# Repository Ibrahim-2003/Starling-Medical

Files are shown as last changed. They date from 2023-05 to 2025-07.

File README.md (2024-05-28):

# Starling Medical Local Repo
This is a repo of the work I did at Starling Medical during my internship. Included in this repo:
- Datasheets of the electronics I used in my projects
- Engineering drawings for manufacturing
- Models of parts and designs I made
- Documentation I wrote for the company
- Notes I took while prototyping and brainstorming
- Research papers I referenced while innovating
- Presentations showcasing my progress and accomplishments
- Programs and software I wrote for the projects

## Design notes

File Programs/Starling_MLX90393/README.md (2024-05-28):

# Adafruit MLX90393 Magnetic Field Sensor Driver Documentation

This driver is for use with the Adafruit MLX90393 Breakout, and has been
designed specifically for these boards:

  ----> https://www.adafruit.com/product/4022

Adafruit invests time and resources providing this open source code,
please support Adafruit and open-source hardware by purchasing
products from Adafruit!

## About this Driver

Originally written by Kevin Townsend for Adafruit Industries. Modified by Ibrahim Al-Akash to meet Starling Medical BPH apparatus requirements.
MIT license, all text above must be included in any redistribution

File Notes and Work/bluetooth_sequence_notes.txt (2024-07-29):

MainActivity.kt
---------------------------------

// onCreate Functions
    BluetoothManagerStateMachine.initialize(applicationContext())
    BluetoothManager2.initialize(applicationContext())
    requestPermissions()

AppSimulationScreen.kt
---------------------------------
Button(
        modifier = Modifier.fillMaxWidth().padding(start = buttonPadding, end = buttonPadding),
        onClick = {
//                navController.previousBackStackEntry?.savedStateHandle?.set("msg", "test data")
//                navController.popBackStack()
        BluetoothManagerStateMachine.startScanning()
        logOutput = "Starting Scan\n" + logOutput
    }) {
        Text(text = "Start")
    }

Gradle
---------------------------------
implementation libs.blessed.kotlin
implementation libs.gson

BluetoothExplorer.kt
---------------------------------
// Press button to turn on scanning in BluetoothManager2
// If the peripheral list in BluetoothManager2 is not empty, display the list of devices using the DeviceNameList which is input to the DeviceNameListHelper
    // Each device gets a DeviceCard using the device name from the DeviceNameListHelper
    // Clicking the DeviceCard stops the scanning in BluetoothManager2, connects to the device using the connectToPeripheral from BluetoothManager2, and navigates to DeviceDetailScreen:
       // BluetoothManager2.stopScanning()
       // val peripheral = BluetoothManager2.peripheralList[index]
       // BluetoothManager2.connectToPeripheral(peripheral)
    // DeviceDetailScreen:
        // Device -> BluetoothManager2.urinDxDeviceCharacteristic
        // Configuration -> BluetoothManager2.urinDxConfigurationCharacteristic
        // Patient -> BluetoothManager2.urinDxPatientCharacteristic
        // Sensors Record {CharacteristicReadInteractionCard} -> BluetoothManager2.urinDxSensorsRecordCharacteristic
        // Network Record {CharacteristicReadInteractionCard} -> BluetoothManager2.urinDxNetworkRecordCharacteristic
        // Battery Record {CharacteristicReadInteractionCard} -> BluetoothManager2.urinDxBatteryRecordCharacteristic
        // Debug {CharacteristicReadInteractionCard} -> BluetoothManager2.urinDxDebugCharacteristic

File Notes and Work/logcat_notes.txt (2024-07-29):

STARTUP SEQUENCE
-----------------------------------------------------------------------------
BluetoothManagerStateMachine,initializing BluetoothHandler
BluetoothManager2,initializing BluetoothHandler
ProfileInstaller,Installing profile for com.starling.bluetoothexplorer
BluetoothAdapter,isLeEnabled(): ON

PRESS START
-----------------------------------------------------------------------------
BluetoothLeScanner,onScannerRegistered() - status=0 scannerId=6 mScannerId=0
BluetoothManagerStateMachine,Found peripheral 'UrinDx' with RSSI -57
BluetoothManagerStateMachine,Connecting to peripheral UrinDx
BluetoothAdapter,isLeEnabled(): ON
BluetoothGatt,connect() - device: CC:11:E1:27:24:1D, auto: false
BluetoothGatt,registerApp()
BluetoothGatt,registerApp() - UUID=1f0445b1-f4ec-49c2-9a09-b407b8ef458b
BluetoothGatt,onClientRegistered() - status=0 clientIf=6
BluetoothGatt,onClientConnectionState() - status=0 clientIf=6 device=CC:11:E1:27:24:1D
BluetoothGatt,discoverServices() - device: CC:11:E1:27:24:1D
BluetoothGatt,onConnectionUpdated() - Device=CC:11:E1:27:24:1D interval=6 latency=0 timeout=500 status=0
BluetoothGatt,onPhyUpdate() - status=0 address=CC:11:E1:27:24:1D txPhy=2 rxPhy=2
BluetoothGatt,onSearchComplete() = Device=CC:11:E1:27:24:1D Status=0
BluetoothManagerStateMachine,Connected to 'UrinDx'
BluetoothManagerStateMachine,Discovered service 00001801-0000-1000-8000-00805f9b34fb
BluetoothManagerStateMachine,Discovered service 00001800-0000-1000-8000-00805f9b34fb
BluetoothManagerStateMachine,Discovered service 0000180f-0000-1000-8000-00805f9b34fb
BluetoothManagerStateMachine,Discovered service 14700001-0eed-456e-a568-7e4e17683148
BluetoothManager,Found characteristic 14700002-0eed-456e-a568-7e4e17683148
BluetoothManagerStateMachine,Discovered service 8d53dc1d-1db7-4cd3-868b-8a527460aa84
BluetoothGatt,requestConnectionPriority() - params: 1
BluetoothGatt,onConnectionUpdated() - Device=CC:11:E1:27:24:1D interval=39 latency=0 timeout=500 status=0
BluetoothGatt,setCharacteristicNotification() - uuid: 14700005-0eed-456e-a568-7e4e17683148 enable: true
BluetoothManagerStateMachine,SUCCESS: Notify set to true for 14700005-0eed-456e-a568-7e4e17683148
BluetoothManagerStateMachine,SUCCESS: Notify set to true for Patient Sample Characteristic
BluetoothGatt,onConnectionUpdated() - Device=CC:11:E1:27:24:1D interval=12 latency=0 timeout=500 status=0
BluetoothGatt,onConnectionUpdated() - Device=CC:11:E1:27:24:1D interval=12 latency=0 timeout=400 status=0
BluetoothManagerStateMachine,Received urinDxPatientSampleCharacteristic
BluetoothManagerStateMachine,[B@92c0d03
BluetoothManagerStateMachine,000051a23aff900100000000000000000000000000000000000000000000000000000000000000000000000000000000000000008c093e074b081404ef064f0b5a093e0748081004ef06390b55093e0747080c04f3061e0b53093e0747080b04f206340b52093e0746080a04f6063a0b51093e0746080a04fb06370b0000000000000000000000000000000000000000000000000000000000000000000000000000000000000000000000000000000000000000000000000000000000000000000000000000000000
BluetoothGatt,onClientConnectionState() - status=19 clientIf=6 device=CC:11:E1:27:24:1D
BluetoothGatt,close()
BluetoothGatt,unregisterApp() - mClientIf=6
BluetoothManagerStateMachine,disconnected 'UrinDx'

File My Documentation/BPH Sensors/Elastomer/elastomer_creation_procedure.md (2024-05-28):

# How to Make an Elastomer for Magnetic BPH Sensor
## Starling Medical
### Ibrahim Al-Akash

# Elastomer Creation Procedure

## Overview
First, model the elastomer with the appropriate geometry for your test. Next, 3D print the elastomer mold. Then, cast the mold using the silicone of the appropriate durometer for your test. Finally, assemble the elastomer with the appropriate magnet for your test.

## Modeling and 3D Printing
1. Design elastomer geometry in SolidWorks. Refer to the file `elastomer_notes.md` or `elastomer_notes.pdf` for further details on how to design an elastomer geometry.
2. Save SolidWorks design as an `.STL` file and import to Chitubox software.
3. In Chitubox software, apply a tilt if possible to the model (for example rotate around z-axis by 45 degrees) and the add supports to model.
4. Ensure the correct resin profile is selected so that the profile matches the resin you will be printing with. Ensure the correct printer is selected in the Chitubox settings.
5. Slice the model and inspect it for any artifacts or errors. If there are errors, try rotating along a different axis and reapplying the supports.
6. Export the slice which will be a `.CTB` file to the directory of your choosing.
7. Upload the exported slice file to a USB flashdrive to send to the 3D printer.
8. Ensure the 3D printer has enough resin to print the parts.
9. Begin the print on the 3D printer.
10. When the 3D print is completed, carefully remove the parts from the plate by using the metal spatula. If the part is stuck, spray a little isopropyl alcohol on it and try again.
11. There should be 3 containers next to the 3D printers labeled `99% Isopropyl Alcohol`, `99% Isopropyl Alcohol (Contaminated)`, and `Diluted Green Wash`. Thoroughly clean the printed parts in each bucket in this order.
12. Set the parts next to the fan and wait ~5 minutes to dry.
13. Place the parts in the water cage in the container at the curing station. Remove the curing plate from the machine and place the water container in its place. Close the lid on it. Make sure the curing machine is set to rotation mode, not light mode. Set the time to 5:00 (6:00 if there are a lot of parts) and let the machine rinse the parts.
14. Once the rinse step is completed, set the parts next to the fan and wait 10 to 15 minutes until they are dry.
15. Once the parts are finished, place the curing plate on the curing machine. Ensure the magnets are aligned correctly so the plate is flush against the base. Ensure the curing machine is set to light mode. Set the time to 5:00 if you are using a VytaFlex or other tin-based silicone. If you are using an ExoFlex or other platinum-based silicone, set the time to as long as possible.
16. Once the curing is completed, carefully remove the supports from the parts using pliers.

## Casting the Silicone Mold
### EcoFlex or Platinum-Based Silicone
1. Spray acryllic lacquer onto the 3D printed molds and ensure any surface that will come into contact with the silicone is sufficiently covered with the lacquer. Wait 24 hours for the acryllic lacquer to cure properly. *This step is critical because platinum-based silicone does not cure well when in contact with the resin. You must disrupt the chemical interaction in order for the silicone to cure properly*.
2. Apply a light coat of MAN200 Releasing Agent to the 3D printed molds.
3. Thoroughly stir Part A and Part B silicones with a popsicle stick prior to dispensing them from their containers. Use separate popsicle sticks for Part A vs. Part B.
4. Ensure you have a scale nearby to measure the Part A and Part B solutions. Place a measuring cup on the scale and tare it. Dispense the appropriate mass of Part A solution into the measuring cup. 
5. Tare the measuring cup with the Part A solution in it. Follow the instructions on the containers to determine the ratio of Part A : Part B by mass. Dispense the appropriate amount of Part B solution into the measuring cup.
6. Thoroghly mix the Part A and Part B mixture using a popsicle stick for 2-3 minutes. The containers for the silicones have a "pot life" specified. This means you can handle the silicones for the specified amount of time before it begins curing.
7. *OPTIONAL*: Place the measuring cup in the vaccum chamber, ensuring the vaccum nozzle is not directly over the cup. Activate the vacuum and wait 3-5 minutes for the bubbles to escape the mixture. *This step is optional, however it produces the best results by removing any bubbles or trapped air from the mixture*.
8. Carefully pour the mixture into the bottom mold until the silicone mixture is flush with the top of the bottom mold. Use a popsicle stick to straighten it out and keep it perfectly flush with the top surface. Then, carefully place the top mold in the approprate position.
9. Wait until the recommended cure time has passed.
10. Carefully open the molds and remove the silicone cast.

### VytaFlex or Tin-Based Silicone
1. Apply a light coat of MAN200 Releasing Agent to the 3D printed molds.
2. Thoroughly stir Part A and Part B silicones with a popsicle stick prior to dispensing them from their containers. Use separate popsicle sticks for Part A vs. Part B.
3. Ensure you have a scale nearby to measure the Part A and Part B solutions. Place a measuring cup on the scale and tare it. Dispense the appropriate mass of Part A solution into the measuring cup. 
4. Tare the measuring cup with the Part A solution in it. Follow the instructions on the containers to determine the ratio of Part A : Part B by mass. Dispense the appropriate amount of Part B solution into the measuring cup.
5. Thoroghly mix the Part A and Part B mixture using a popsicle stick for 2-3 minutes. The containers for the silicones have a "pot life" specified. This means you can handle the silicones for the specified amount of time before it begins curing.
6. *OPTIONAL*: Place the measuring cup in the vaccum chamber, ensuring the vaccum nozzle is not directly over the cup. Activate the vacuum and wait 3-5 minutes for the bubbles to escape the mixture. *This step is optional, however it produces the best results by removing any bubbles or trapped air from the mixture*.
7. Carefully pour the mixture into the bottom mold until the silicone mixture is flush with the top of the bottom mold. Use a popsicle stick to straighten it out and keep it perfectly flush with the top surface. Then, carefully place the top mold in the approprate position.
8. Wait until the recommended cure time has passed.
9. Carefully open the molds and remove the silicone cast.

## Elastomer Assembly
1. Acquire the appropriate magnet for the elastomer and ideally get a magnetic compass to help with properly orienting the magnet prior to adhering it to the elastomer.
2. Ensure the magnet is oriented so that the side of the magnet that attracts the needle North on the compass is facing the sensor as shown in the diagram below:

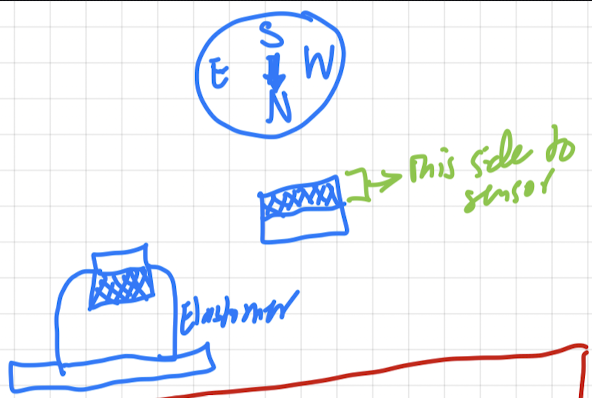
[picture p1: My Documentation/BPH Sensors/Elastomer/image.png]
Magnet Orientation


Alternatively, if you do not have a compass, have the magnetometer sensor running and make sure the magnet is oriented in a way that produces positive B-field values in the magnetometer z-axis data. *This is a very important step. Remember, measure twice and cut once. You must ensure you are certain that the magnet orientation is correct before moving onto the next step*.
3. Apply just enough super glue to adequately cover the surface of the magnet in contact with the elastomer.
4. Wait 10-30 minutes for the super glue to cure.

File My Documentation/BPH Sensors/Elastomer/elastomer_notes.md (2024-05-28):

# How to Design an Elastomer for Magnetic BPH Sensor
## Starling Medical
### Ibrahim Al-Akash

# Elastomer Design Notes

## Overview
To design a proper elastomer for the magnetometer BPH sensor, you must first determine the geometry you want to test, model the elastomer, and model the elastomer mold.

## Elastomer Geometry
Elastomer geometry is important in determining the magnetometer sensitivity. Some basic principles to keep in mind are the following:

- Shorter elastomers are more malleable, however, the magnet has a smaller range of distances it can move. This limits the range of masses the sensor can detect.

- Thicker elastomers enable the magnet to move a larger range of distances, however, they are more rigid. This limits the sensitivity of the magnet, which translates to a lower resolution of masses it can detect (ex: $\pm$ 0.01g vs. $\pm$ 5g).

- Elastomers with a larger surface area in contact with the water will require more water to deform. An equation that is important to keep in mind is $Pressure=\frac{Force}{Area}$. Force is the mass of the water and area is the area of the elastomer in contact with the water. If the area is too large, a very large force will be required to supply adequate pressure to compress the elastomer, which means more water must be added.

- Elastomers with high durometer rating will be harder to compress, and require either more water or a smaller area in contact with the water.

- Elastomers with larger magnets will enable the sensor to read a wider range of masses, however this comes at the price of sensitivity. This limits the resolution of the sensor. This is due to the fact that stronger magnets can reach a farther distance from the sensor before their B-field begins to drop off significantly. The B-field of a weaker magnet drops off very rapidly when moving only a small distance. This makes it more sensitive, however it comes at the cost of range.

- The researchers who wrote the paper on this technology recommend embedding the magnet in the top of the elastome to prevent hysterisis and creep from infecting the magnet and introducing noise to the data over time.

## Modeling the Elastomer
Prior to modeling the elastomer mold, I recommend modeling the elastomer as you would like it to look when the silicone is fully cured. Make sure you do not forget to include a notch so that the magnet can be flush with the top surface of the elastomer. By modeling the elastomer before the mold, you can easily calculate dimensions and evaluate mass and other properties to better inform your design decisions.

## Modeling the Elastomer Mold
For some elastomer designs, you can make a 1-piece mold. These are elastomers in which only 1 surface has an indentation (the surface containing the magnet). If you are making an elastomer in which both the top and bottom surfaces have indentations or notches, you need to make a 2-piece mold.

### 1-Piece Mold
1. Measure the elastomer dimensions using the `Evaluate` tool in SolidWorks.
2. Make a block with some leeway for the dimensions of the elastomer. For example, if you are making an elastomer that is $5\times5\times5mm^3$, make the block $10\times10\times10mm^3$.
This makes it easier to work with the 3D print and prevents you from accidentally cracking the printed mold due to it being to thin and fragile.
3. Make an assembly with the block and the elastomer model.
4. Create a mold into the block using the elastomer model with the notch facing inward into the block and the flat surface of the elastomer flush with the flat surface of the block.

### 2-Piece Mold
1. Measure the elastomer dimensions using the `Evaluate` tool in SolidWorks.
2. Make the bottom mold, by creating a block and then manually drawing sketches and extrude cutting.
3. To Make the top mold, I recommend making a flat part that is flush with the top surface of the bottom mold, and then extruding out the piece which will make the notch for the magnet. This makes it easier when manufacturing since you can pour the silicone into the bottom mold and then press the top mold into the bottom one.

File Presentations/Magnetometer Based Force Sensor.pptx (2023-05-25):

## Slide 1

Method | Price | Sensitivity | Size | Power
Silicone Elastomer | Magnetometer - $9.99 Si - $0.01 Magnet - $0.10 | 1 mN resolution Range goes up to at least 2.6 N | 3mm x 3mm x 0.8mm | 100uW to 10mW

## Introduction

- The differential pressure sensor has shown promise, however 2 main issues
  1. High cost compared to other sensor techniques ($20/sensor)
  2. Potential issues down the line with sedimentation or corrosion
- Magnetometer-based force sensor solves these issues
  - Low cost ($1.85/sensor)
  - No sedimentation issues
  - Ultra-low power consumption (100uW to 10mW)
  - High resolution (1 mN)

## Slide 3

Magnetic Pressure Sensor

Force from urine stream causes shear and normal stress on elastomer, bringing the magnet closer/farther from the magnetometer. Magnetic field changes then corresponds to applied force

Neodymium Magnet

Silicon Elastomer

Magnetometer

Urine Stream

Fx

d1

Fz

Fy

Deformation

Neodymium Magnet

Silicon Elastomer

Magnetometer

d2

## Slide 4

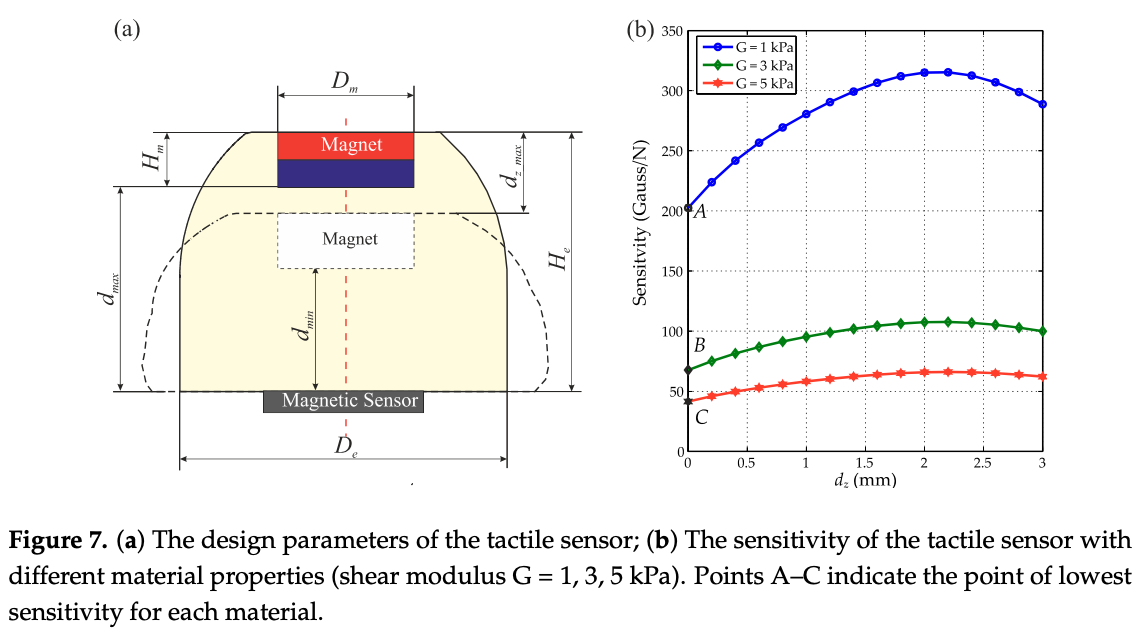
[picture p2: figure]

## Manufacturing Process

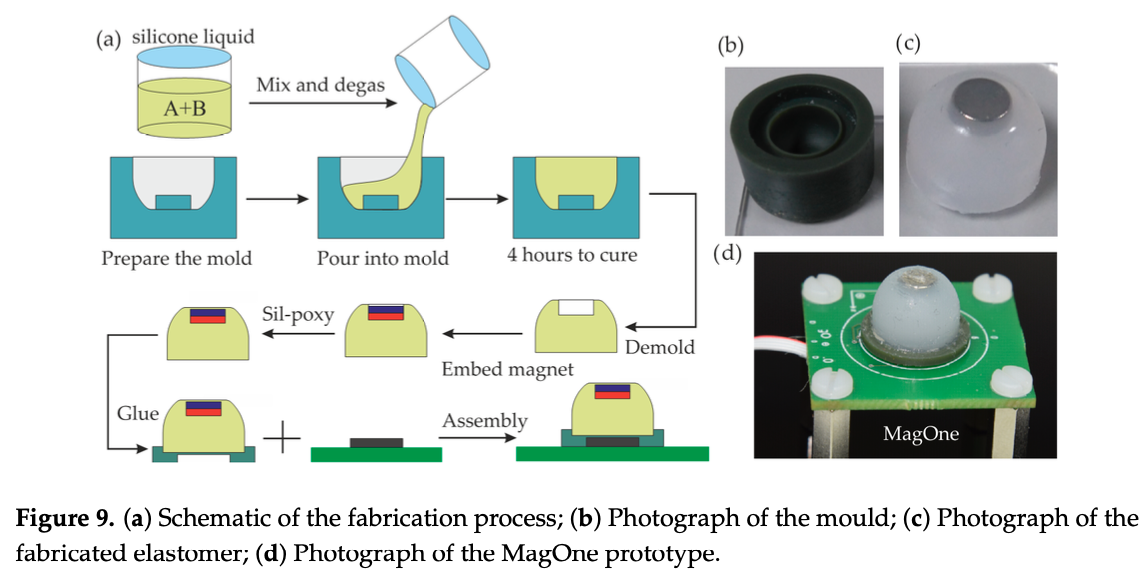
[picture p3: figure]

1. 3D Print Mold for Elastomer
2. Pour Elastomer (Si) into Mold and Cure
3. Attach the neodymium magnet to the indentation in the elastomer mold using Sil-poxy
4. Connect assembly to PCB using adhesives

## CAD Model

Neodymium Magnet

PCB Waterproof Casing

Silicon Elastomer

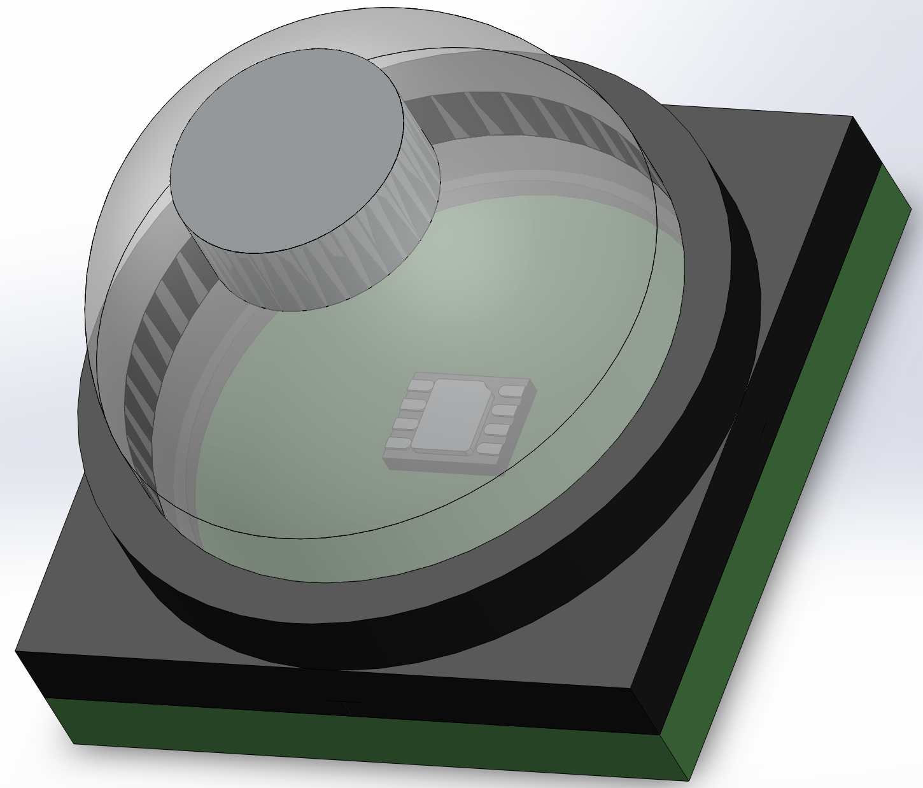
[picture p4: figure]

11.22mm

Magnetometer Sensor

14mm

PCB

14mm

## Further Considerations

- May be difficult to manufacture, since Si elastomer must be prepared manually
- Elastomer can deform over time due to creep effects, however the geometry of the elastomer and placement of the magnet at the top mitigates this
- Lots of testing required and many different configurations (ie. Elastomer material, elastomer geometry, magnet size, magnetometer)
- Tilting of magnet can cause inaccuracies – can be mitigated with IMU MEMS sensor

## Prototype

To test the viability of this solution and compare performance with other sensor prototypes, I propose assembling a magnetic elastomer force sensor and testing the accuracy in a controlled environment
The test will be:
1. Using a water bottle, pour water onto the elastomer sensor using 2 test variations: 1) constant rate (simulating healthy) and 2) sputtering (simulating BPH)
2. Record the magnetometer data locally, either directly to the computer or on an SD card connected to the microcontroller
3. Record the true flow rate using the mass scale
4. Using the LSTM model from Mikayla’s rig, fit the data
5. Test the LSTM results

## Prototype Materials

Item | Cost
Neodymium Magnets (5mm x 2mm) (https://www.first4magnets.com/us/circular-disc-rod-c34/n35-neodymium-disc-magnet-5mm-dia-x-2mm-thick-1-12lbs-pull-p6698) | $6.99
Magnetometer (https://www.mouser.com/new/melexis/melexis-MLX90393-triaxis-micropower-magnetometer/) | $1.85
Microcontroller | Available in lab
Silicon (https://www.googleadservices.com/pagead/aclk?ai=DChcSEwjLlO3P-o7_AhURHX0KHbL1AXkYABAKGgJwdg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) | $42.99 (2lbs)
Sil-poxy (https://www.googleadservices.com/pagead/aclk?ai=DChcSEwimzsPl-o7_AhUJAK0GHSWsAYEYABALGgJwdg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) | $5.98
Silicon Releasing Agent (https://www.amazon.com/Silicone-Release-Spray-Agent-Aerosol/dp/B085CBSS5Y) | $16.99
3D-print | Available in lab

Total Cost of Materials: $74.80

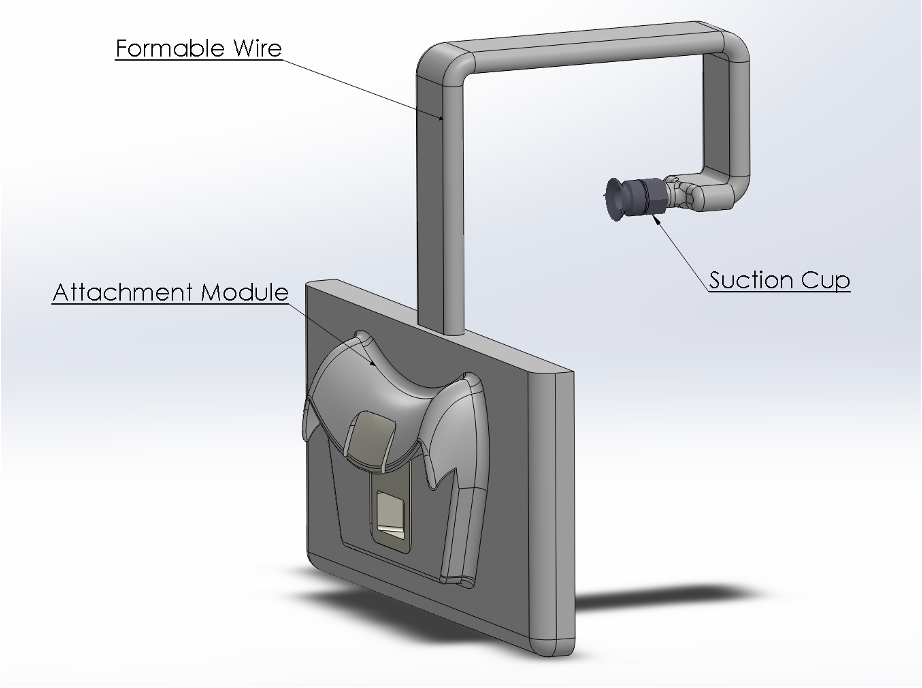
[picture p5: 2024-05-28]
Models/Attachment Anchor Designs/External Suction Cup.png

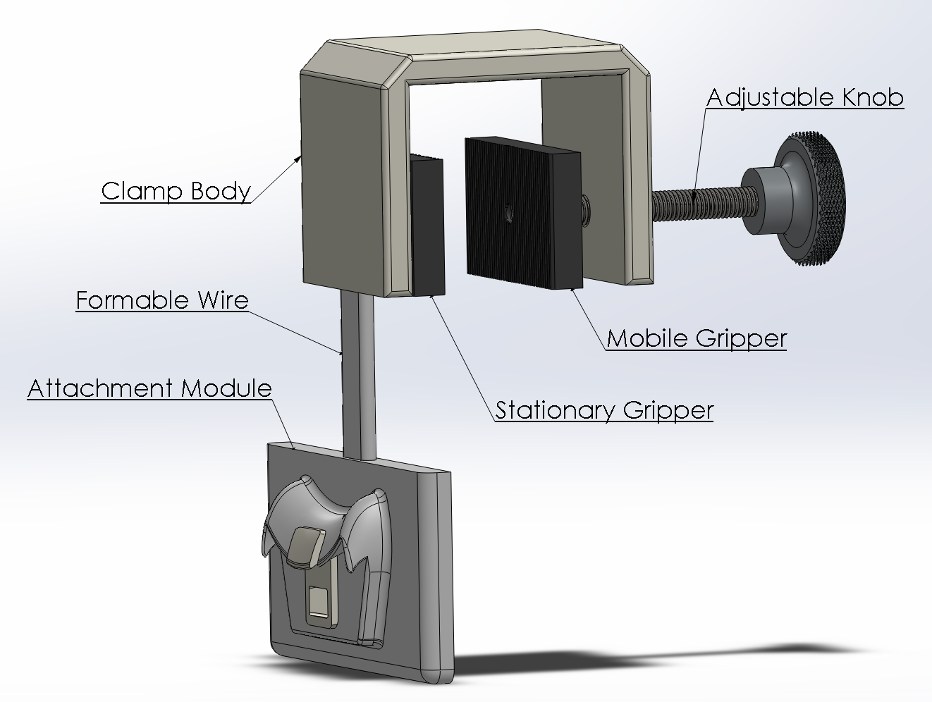
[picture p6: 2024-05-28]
Models/Attachment Anchor Designs/Mechanical Clamp.png

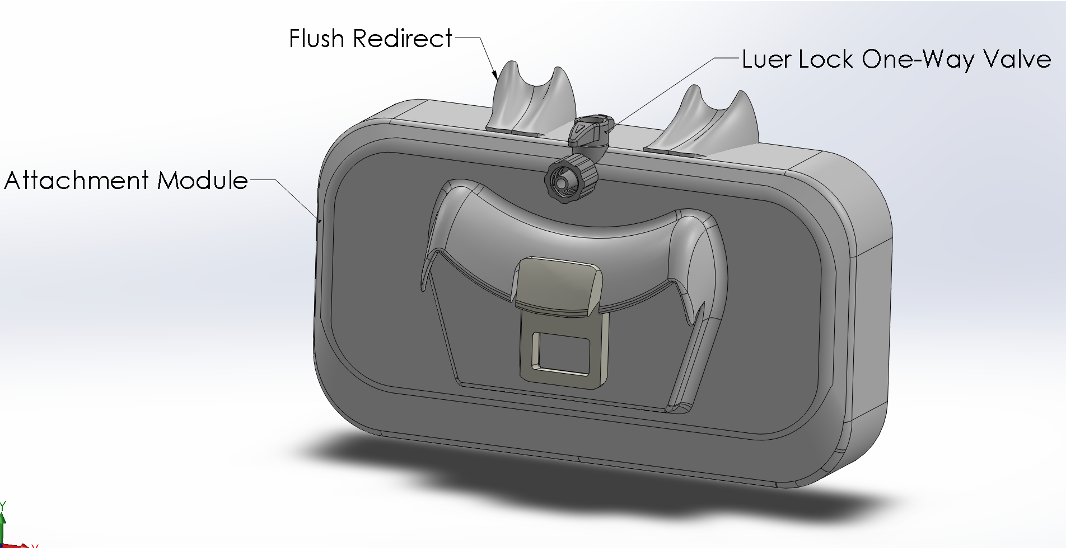
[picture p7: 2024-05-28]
Models/Attachment Anchor Designs/Internal Suction Cup.png

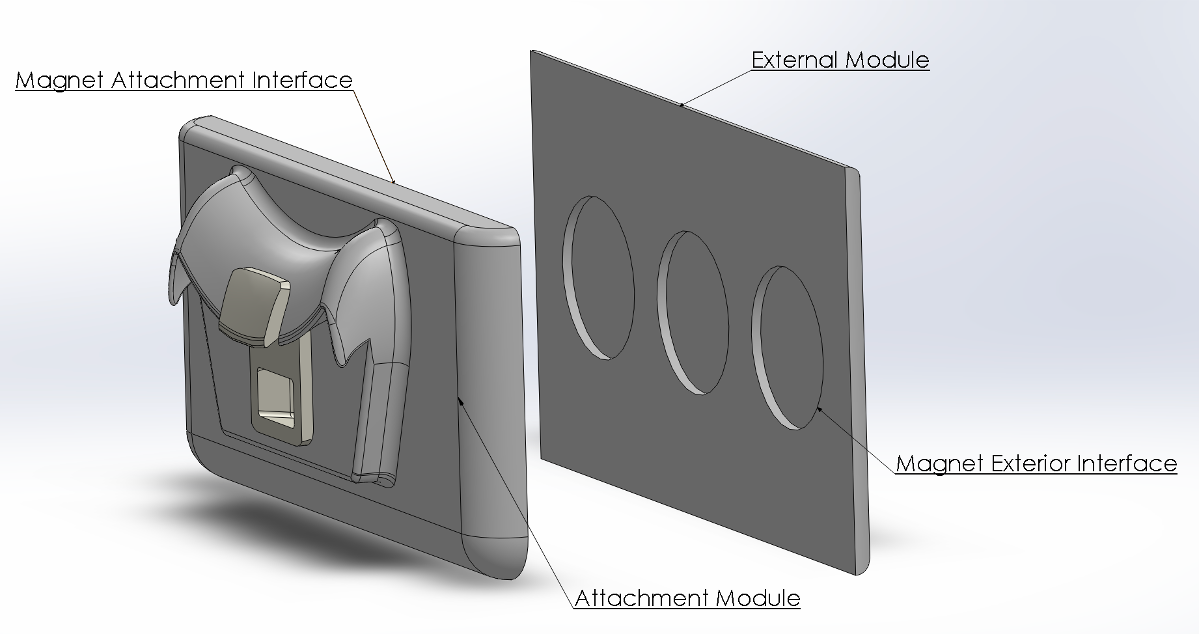
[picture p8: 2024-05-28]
Models/Attachment Anchor Designs/Magnetic Attachment.png

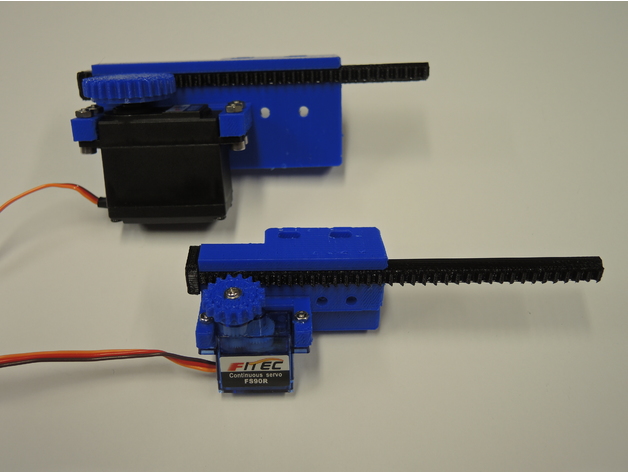
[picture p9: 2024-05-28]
Models/Downloads/Linear_Servo_Actuators_3170748/images/f9ad5a70d2f492784202931d99d89c06.JPG

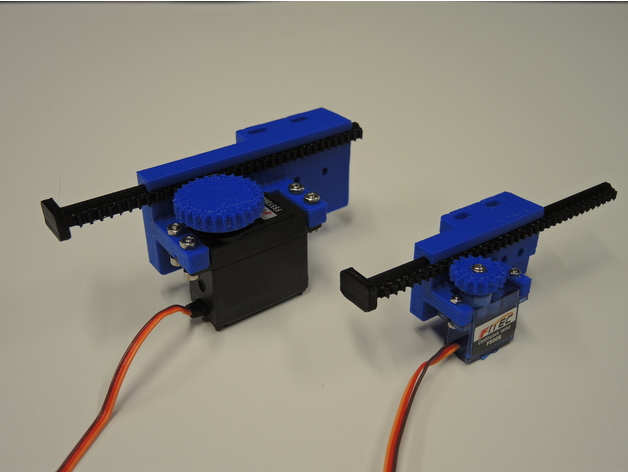
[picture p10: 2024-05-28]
Models/Downloads/Linear_Servo_Actuators_3170748/images/db6269659dbf2e3b0a1140e914c5139f.JPG

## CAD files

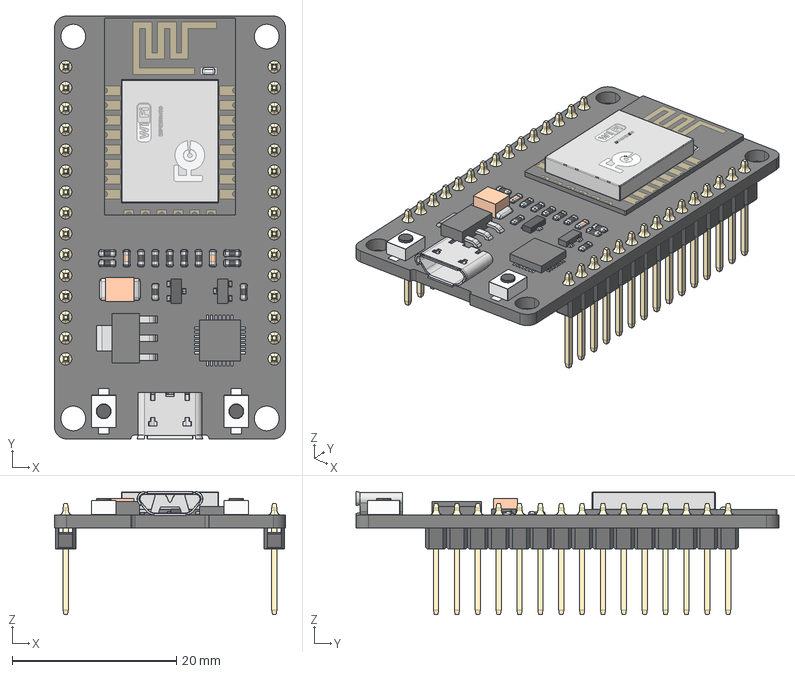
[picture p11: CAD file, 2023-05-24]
Models/BPH Sensors/Differential Pressure Guage Device/esp32-dev-kit-v1-1.snapshot.3/esp32_dev_kit_v1_asm.stp
28.1 x 51.5 x 15.0 mm
PCB
PIN x 30
WIFI_CARD_2
RECTANGULARCHIP_2
MICROCHIP_2
TANCHIP_2
TRANSISTOR_3-LEG_2
RESISTOR1_2 x 11
RESISTOR2-32_2 x 2
TRANSISTOR_3-LEG2_2
BUTTONFLASH-13_2 x 2
BUTTONFLASH-14_2 x 2
USB_SOCKET_2

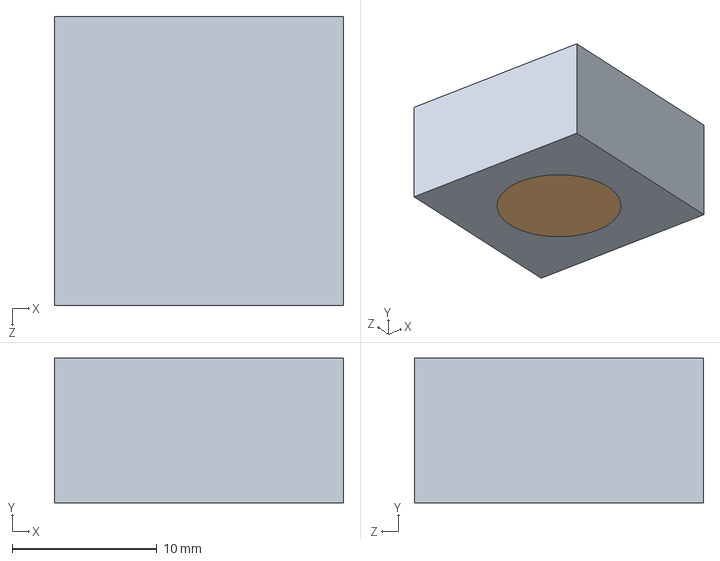
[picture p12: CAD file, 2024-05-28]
Models/BPH Sensors/Magnetic Force Sensor Device/Elastomer Mold.SLDASM
20.0 x 10.0 x 20.0 mm
Elastomer Mold
Silicon Elastomer

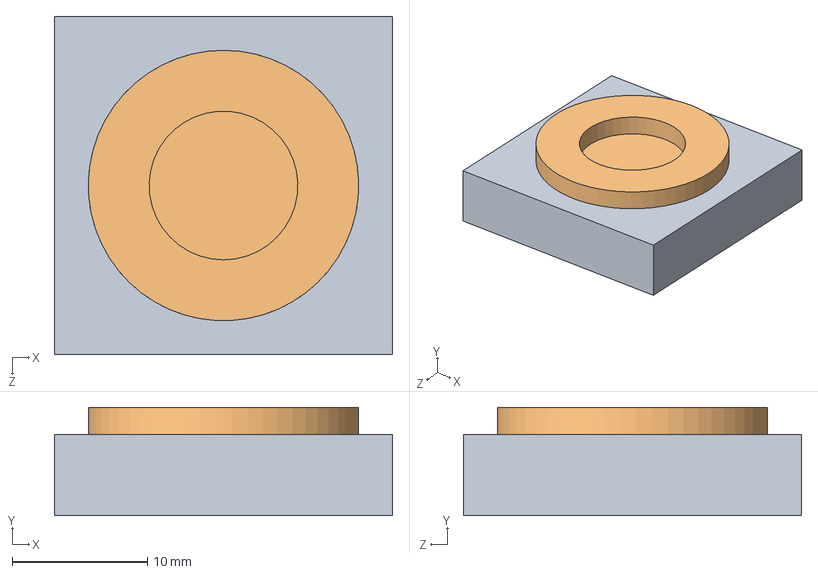
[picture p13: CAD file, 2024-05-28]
Models/BPH Sensors/Magnetic Force Sensor Device/Experiment Test Apparatus/Elastomer Experiments/Molds/C_10m_5t/C_10m_5t_mold_bottom.SLDASM
25.0 x 8.00 x 25.0 mm
C_10m_5t_mold
C_10m_5t

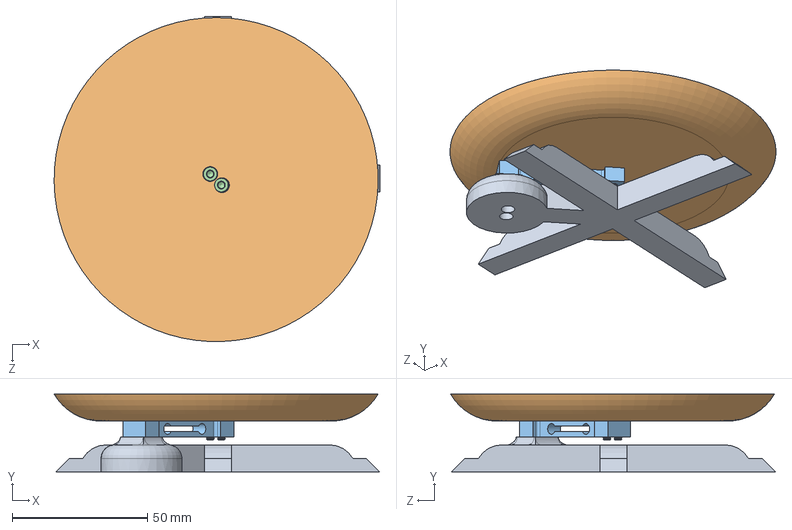
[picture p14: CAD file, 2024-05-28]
Models/BPH Sensors/Magnetic Force Sensor Device/Experiment Test Apparatus/Load Cell Assembly.SLDASM
120.6 x 28.8 x 120.4 mm
Load Cell Bottom
Load Cell Top
Load Cell Bar
M3x12_Socket_Stainless_Steel_Screw x 4

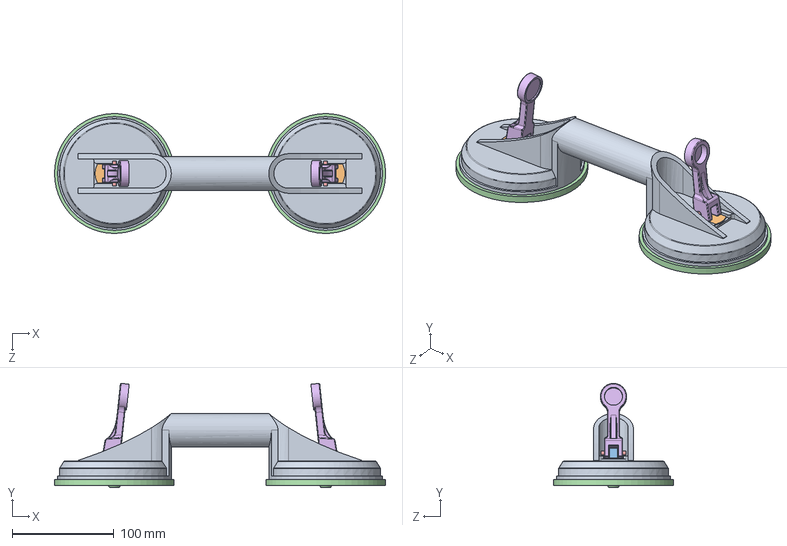
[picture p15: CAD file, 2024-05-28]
Models/Downloads/cup-suction-lifter-1.snapshot.9/4000-817214_Suction Lifter/4000-817214_2-Cup Suction Lifter.SLDASM
325.9 x 102.6 x 118.0 mm
4000-817214_Body
4000-817214_Washer x 2
4000-817214_Shaft x 2
4000-817214_Cup x 2
4000-817214_Splint x 2
4000-817214_Lever x 2

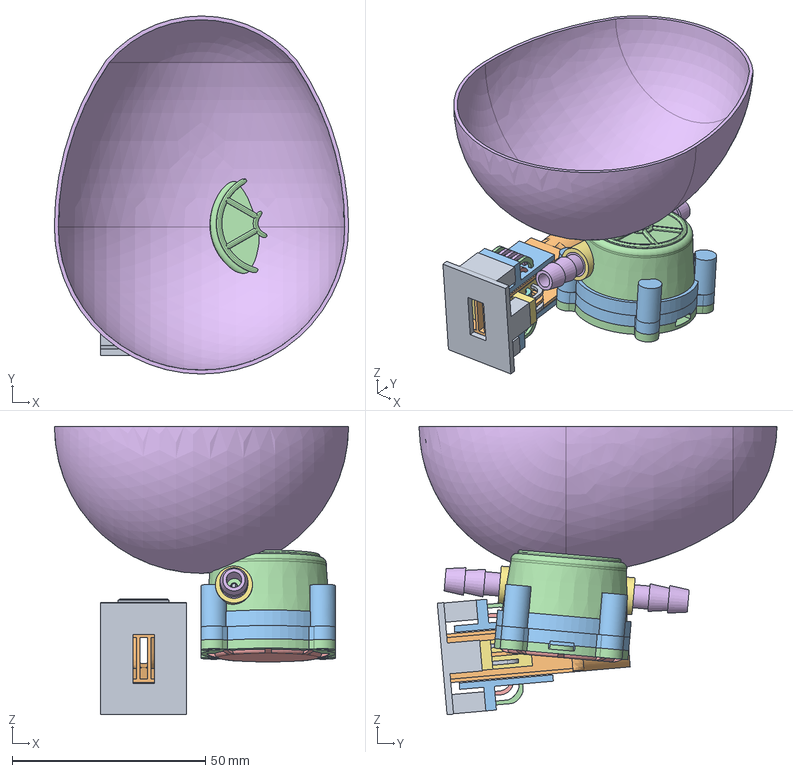
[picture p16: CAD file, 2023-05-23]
Models/Downloads/UrinDx Assembly.step
76.2 x 92.7 x 74.7 mm
Board
Cuvette
5 Pin Sensor x 2
3 Pin Sensor x 2
YF-S401 Base
Impellor
YF-S401 Spacer
YF-S401 Cap
Adam Funnel

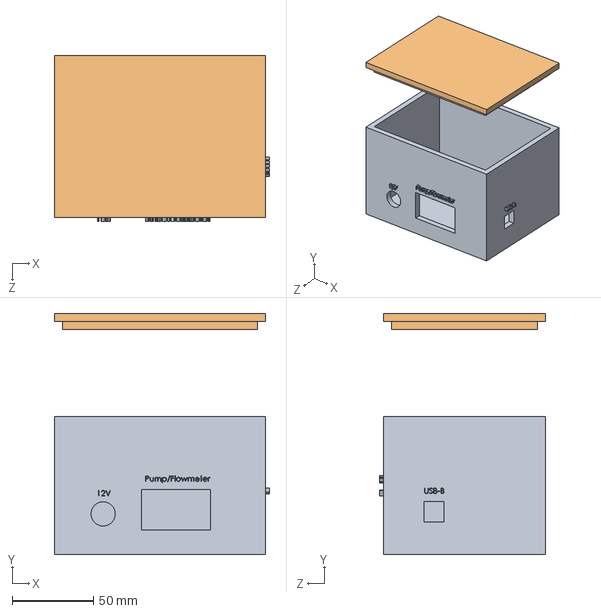
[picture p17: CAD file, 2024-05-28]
Models/Urinator Testing Apparatus/Circuit Container Assembly.SLDASM
132.5 x 148.4 x 102.5 mm
Circuit Box
Circuit Box Cover

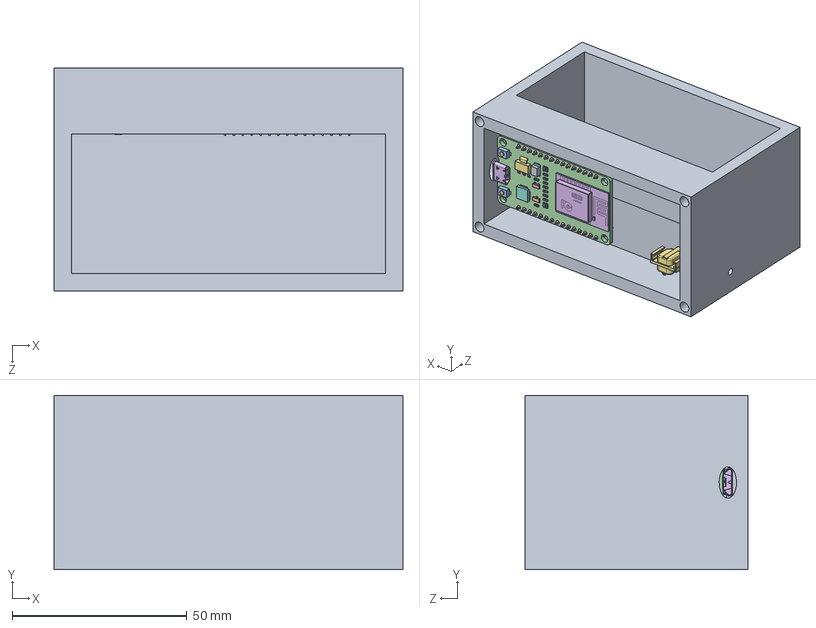
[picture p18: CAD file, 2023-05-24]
Models/BPH Sensors/Differential Pressure Guage Device/Differential Pressure Device Assembly.SLDASM
100.0 x 50.0 x 64.0 mm
Pythagoras Container
BUTTONFLASH-13_2.stp x 2
BUTTONFLASH-14_2.stp x 2
PCB.stp
PIN.stp x 30
WIFI_CARD_2.stp
RECTANGULARCHIP_2.stp
MICROCHIP_2.stp
TANCHIP_2.stp
TRANSISTOR_3-LEG_2.stp
RESISTOR1_2.stp x 11
RESISTOR2-32_2.stp x 2
TRANSISTOR_3-LEG2_2.stp
USB_SOCKET_2.stp
Differential Pressure Sensor

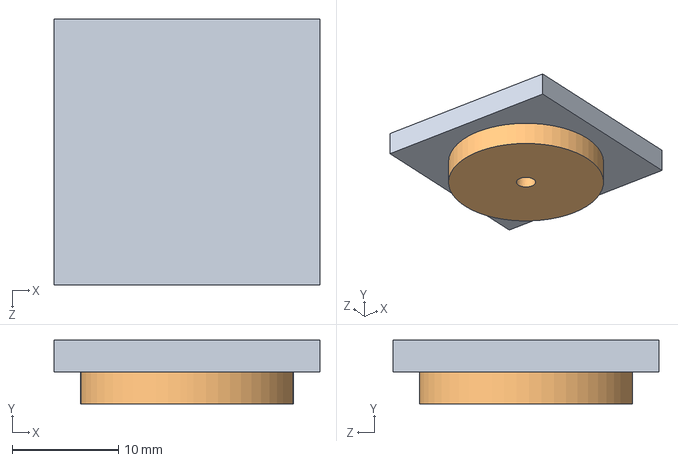
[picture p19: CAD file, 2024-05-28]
Models/BPH Sensors/Magnetic Force Sensor Device/Experiment Test Apparatus/Elastomer Experiments/Molds/C_10m_5t/C_10m_5t_mold_top.SLDASM
25.0 x 6.00 x 25.0 mm
25x25x5_block
C_10m_5t

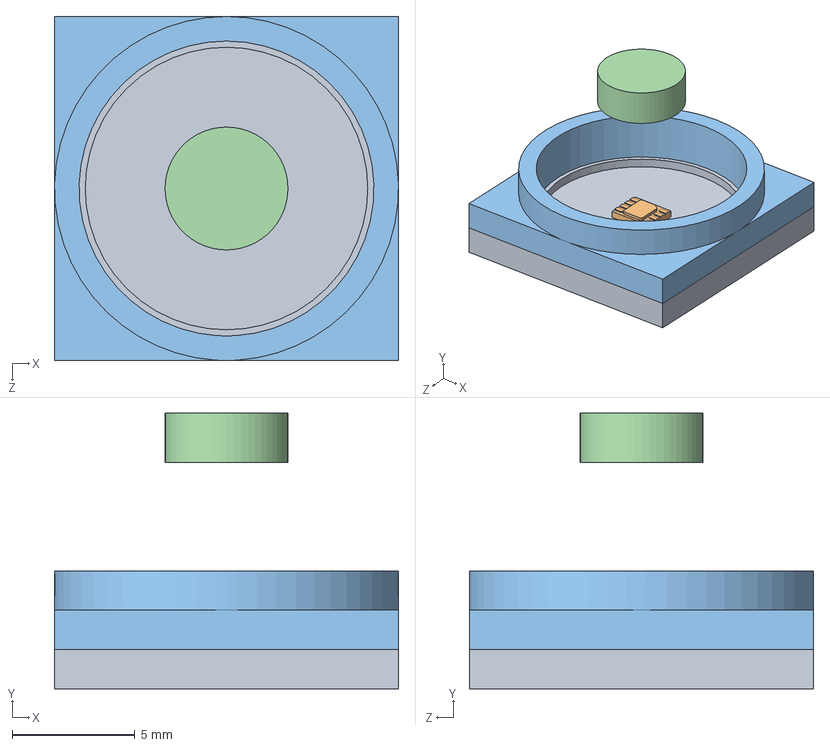
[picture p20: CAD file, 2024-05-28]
Models/BPH Sensors/Magnetic Force Sensor Device/Magnetic Force Sensor Assembly.SLDASM
14.0 x 11.2 x 14.0 mm
PCB with O-Ring
MLX90393 Magnetometer
Elastomer PCB Interface
Neodymium Magnet

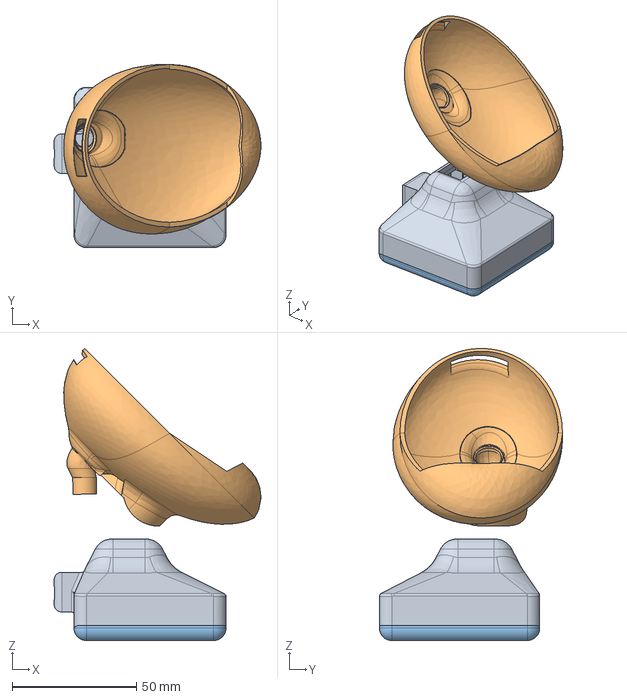
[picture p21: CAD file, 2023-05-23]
Models/Downloads/Assembly.step
83.3 x 73.8 x 117.6 mm
casingtop_v8_
funnelravamp_

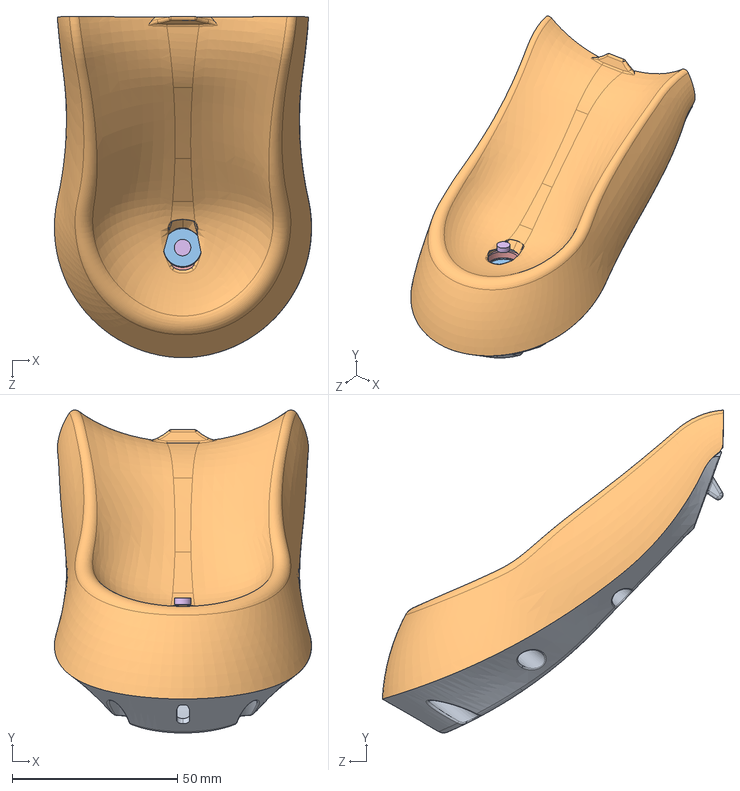
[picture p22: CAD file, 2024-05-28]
Models/BPH Sensors/Magnetic Force Sensor Device/Magnetic Force Sensor with UrinDX Casing Assembly.SLDASM
77.9 x 97.9 x 103.5 mm
UrinDX Bottom Housing
UrinDX Top Housing
PCB with O-Ring
MLX90393 Magnetometer
Elastomer PCB Interface
Neodymium Magnet

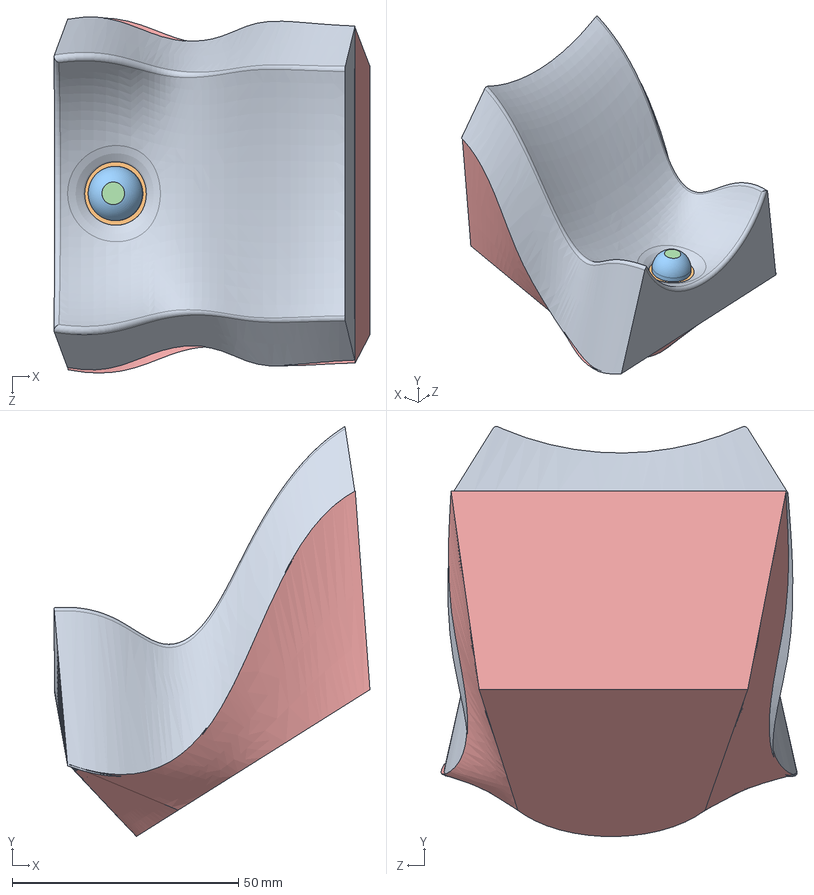
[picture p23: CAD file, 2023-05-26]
Models/BPH Sensors/Magnetic Force Sensor Device/Full Device with Both Casings.SLDASM
69.7 x 90.5 x 78.6 mm
Funnel with Opening for Elastomer
Elastomer PCB Interface
Silicon Elastomer
Neodymium Magnet
Electronics Case UrinDX Tagleed

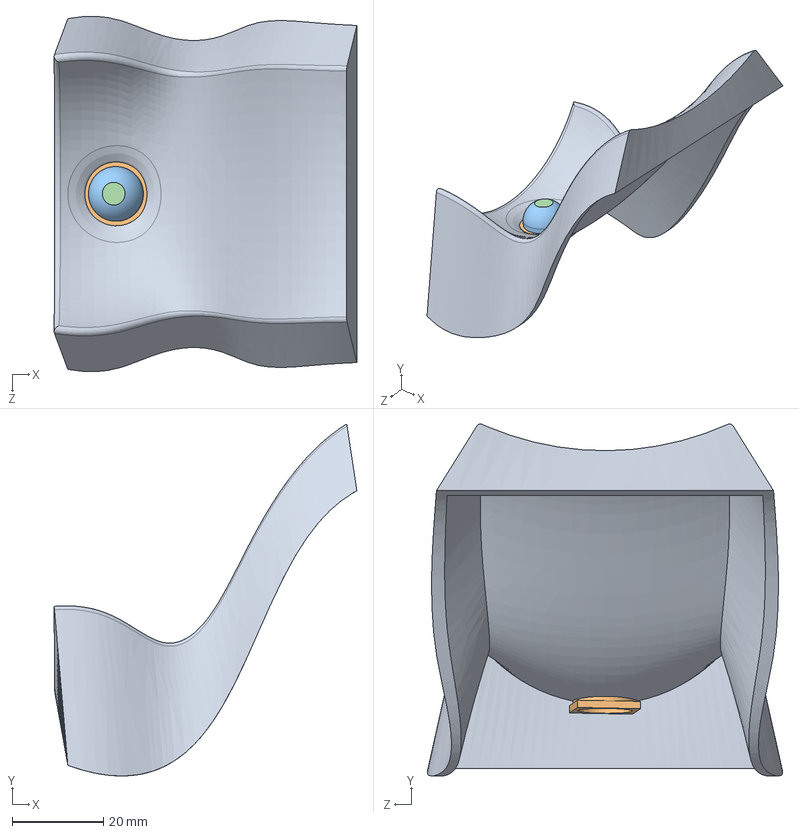
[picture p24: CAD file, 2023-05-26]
Models/BPH Sensors/Magnetic Force Sensor Device/Magnetic Force Sensor with Casing Assembly.SLDASM
66.5 x 77.3 x 78.0 mm
Funnel with Opening for Elastomer
Elastomer PCB Interface
Silicon Elastomer
Neodymium Magnet

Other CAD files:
Models/BPH Sensors/Differential Pressure Guage Device/Dynamic Water Test DP V2.SLDPRT
Models/BPH Sensors/Magnetic Force Sensor Device/Experiment Test Apparatus/Elastomer Experiments/Molds/C_10m_8t/C_10m_8t_bottom.SLDPRT
Models/BPH Sensors/Magnetic Force Sensor Device/Experiment Test Apparatus/Elastomer Experiments/Molds/C_5m_5t/C_5m_5t_top.SLDPRT
Models/BPH Sensors/Magnetic Force Sensor Device/Experiment Test Apparatus/Elastomer Experiments/Molds/C_5m_7t/C_5m_7t_top.SLDPRT
Models/BPH Sensors/Differential Pressure Guage Device/Differential Pressure Sensor.SLDPRT
Models/BPH Sensors/Differential Pressure Guage Device/Dynamic Water Test DP V1.SLDPRT
Models/BPH Sensors/Differential Pressure Guage Device/Pythagoras Container.SLDPRT
Models/BPH Sensors/Differential Pressure Guage Device/Static Water Test DP V1.SLDPRT
Models/BPH Sensors/Magnetic Force Sensor Device/Elastomer Mold.SLDPRT
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

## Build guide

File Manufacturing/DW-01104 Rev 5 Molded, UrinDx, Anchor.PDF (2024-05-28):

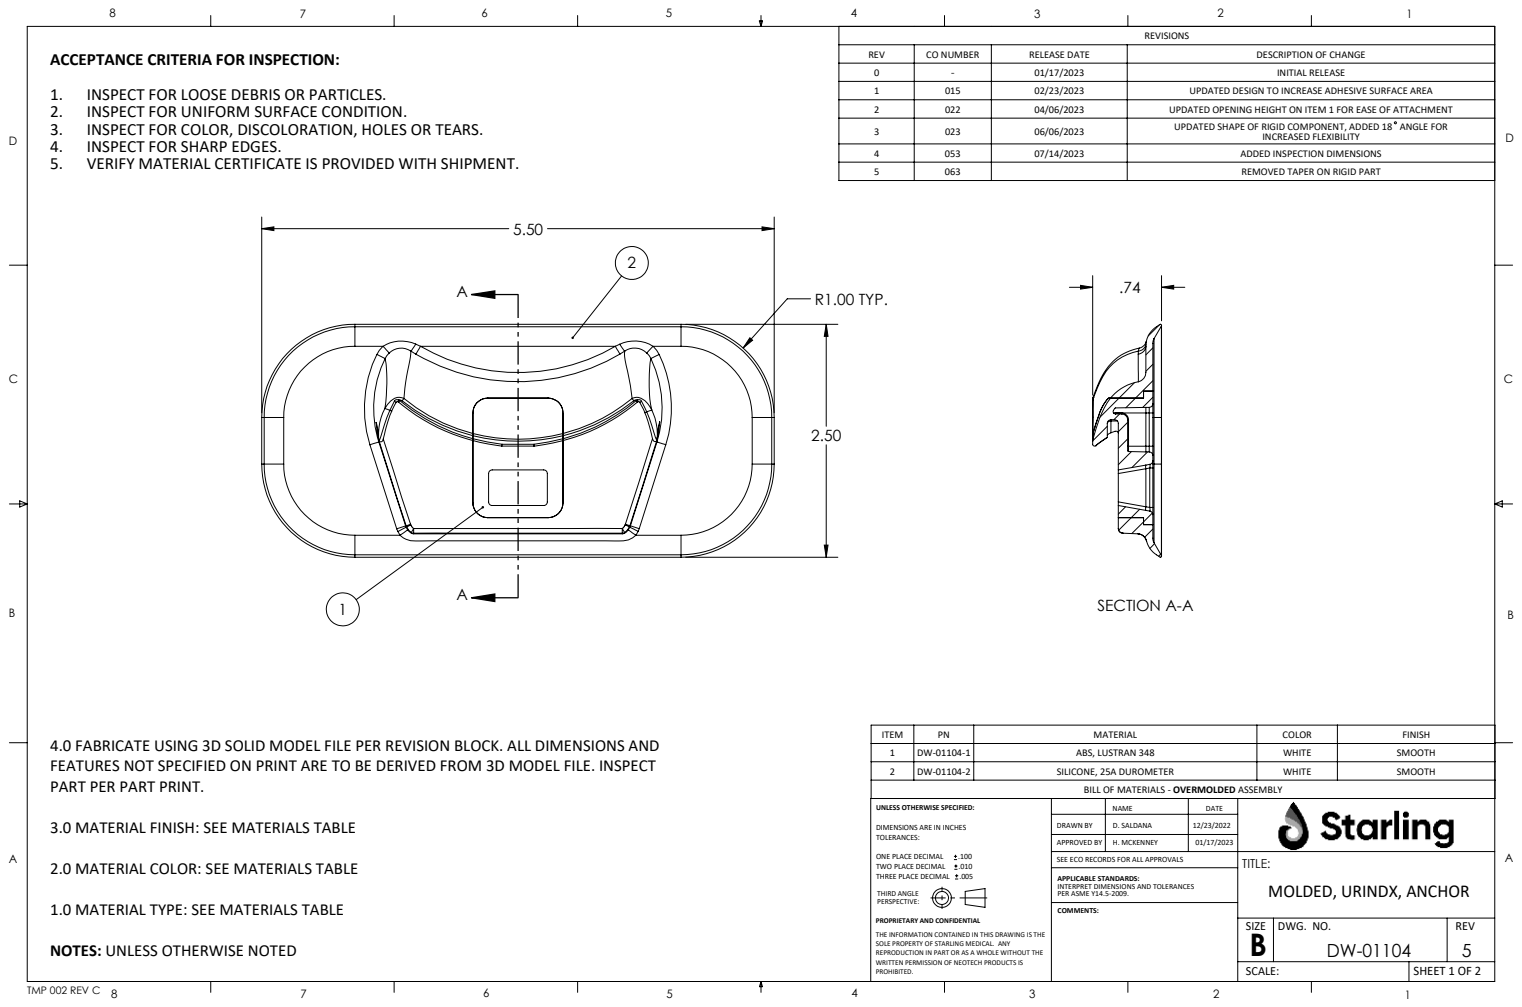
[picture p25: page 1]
R1.00 TYP.; SECTION A-A; D. SALDANA; SHEET 1 OF 2; DWG. NO.; REV; MOLDED, URINDX, ANCHOR; TMP 002 REV C; ONE PLACE DECIMAL; TWO PLACE DECIMAL; THREE PLACE DECIMAL .005; APPLICABLE STANDARDS:; H. MCKENNEY

ACCEPTANCE CRITERIA FOR INSPECTION:
1. INSPECT FOR LOOSE DEBRIS OR PARTICLES.
2. INSPECT FOR UNIFORM SURFACE CONDITION.
3. INSPECT FOR COLOR, DISCOLORATION, HOLES OR TEARS.
4. INSPECT FOR SHARP EDGES.
5. VERIFY MATERIAL CERTIFICATE IS PROVIDED WITH SHIPMENT.

REV | CO NUMBER | RELEASE DATE | DESCRIPTION OF CHANGE
0 | - | 01/17/2023 | INITIAL RELEASE
1 | 015 | 02/23/2023 | UPDATED DESIGN TO INCREASE ADHESIVE SURFACE AREA
2 | 022 | 04/06/2023 | UPDATED OPENING HEIGHT ON ITEM 1 FOR EASE OF ATTACHMENT
3 | 023 | 06/06/2023 | UPDATED SHAPE OF RIGID COMPONENT, ADDED 18 ANGLE FOR INCREASED FLEXIBILITY

4 | 053 | 07/14/2023 | ADDED INSPECTION DIMENSIONS
5 | 063 | | REMOVED TAPER ON RIGID PART

ITEM | PN | MATERIAL | COLOR | FINISH
1 | DW-01104-1 | ABS, LUSTRAN 348 | WHITE | SMOOTH
2 | DW-01104-2 | SILICONE, 25A DUROMETER | WHITE | SMOOTH

4.0 FABRICATE USING 3D SOLID MODEL FILE PER REVISION BLOCK. ALL DIMENSIONS AND
FEATURES NOT SPECIFIED ON PRINT ARE TO BE DERIVED FROM 3D MODEL FILE. INSPECT
PART PER PART PRINT.
3.0 MATERIAL FINISH: SEE MATERIALS TABLE
2.0 MATERIAL COLOR: SEE MATERIALS TABLE
1.0 MATERIAL TYPE: SEE MATERIALS TABLE
NOTES: UNLESS OTHERWISE NOTED

BILL OF MATERIALS - OVERMOLDED ASSEMBLY

UNLESS OTHERWISE SPECIFIED:
DIMENSIONS ARE IN INCHES
TOLERANCES:
THIRD ANGLE
PERSPECTIVE:
PROPRIETARY AND CONFIDENTIAL
THE INFORMATION CONTAINED IN THIS DRAWING IS THE
SOLE PROPERTY OF STARLING MEDICAL. ANY
REPRODUCTION IN PART OR AS A WHOLE WITHOUT THE
WRITTEN PERMISSION OF NEOTECH PRODUCTS IS
PROHIBITED.

DRAWN BY
APPROVED BY
SEE ECO RECORDS FOR ALL APPROVALS

INTERPRET DIMENSIONS AND TOLERANCES
PER ASME Y14.5-2009.
COMMENTS:

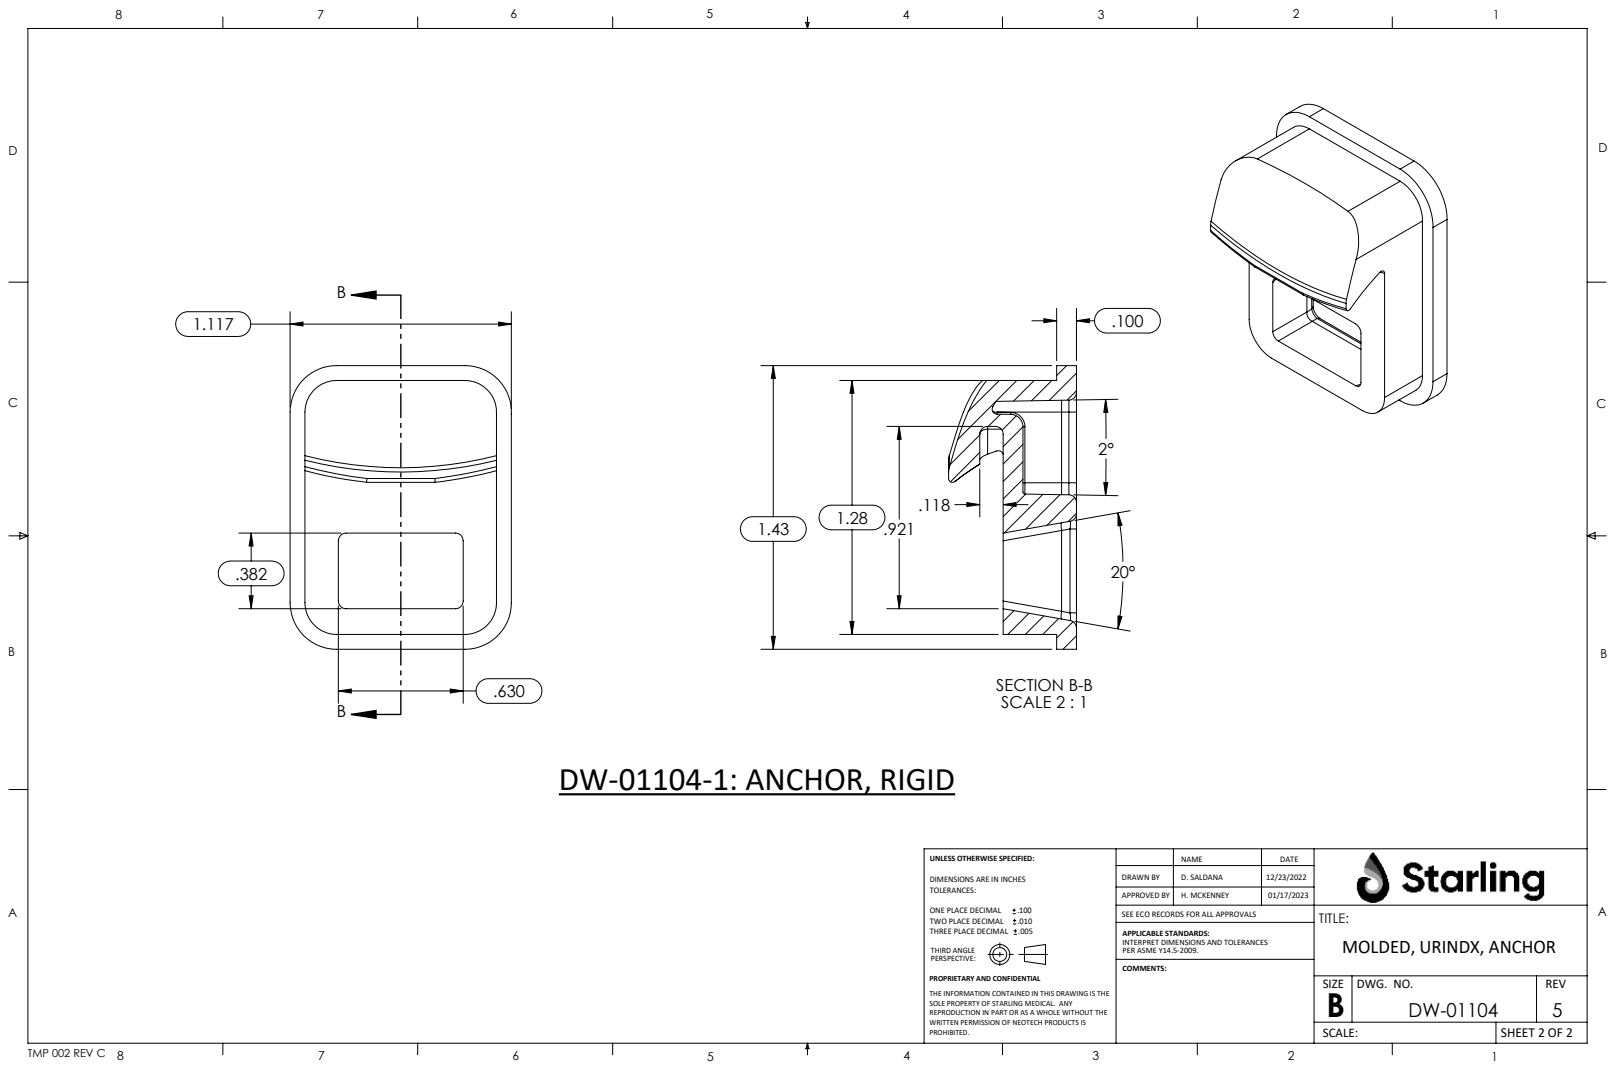
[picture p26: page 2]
SECTION B-B SCALE 2 : 1; D. SALDANA; SHEET 2 OF 2; DWG. NO.; REV; MOLDED, URINDX, ANCHOR; TMP 002 REV C; ONE PLACE DECIMAL; TWO PLACE DECIMAL; THREE PLACE DECIMAL .005; APPLICABLE STANDARDS:; H. MCKENNEY

DW-01104-1: ANCHOR, RIGID

UNLESS OTHERWISE SPECIFIED:
DIMENSIONS ARE IN INCHES
TOLERANCES:
THIRD ANGLE
PERSPECTIVE:
PROPRIETARY AND CONFIDENTIAL
THE INFORMATION CONTAINED IN THIS DRAWING IS THE
SOLE PROPERTY OF STARLING MEDICAL. ANY
REPRODUCTION IN PART OR AS A WHOLE WITHOUT THE
WRITTEN PERMISSION OF NEOTECH PRODUCTS IS
PROHIBITED.

DRAWN BY
APPROVED BY
SEE ECO RECORDS FOR ALL APPROVALS

INTERPRET DIMENSIONS AND TOLERANCES
PER ASME Y14.5-2009.
COMMENTS:

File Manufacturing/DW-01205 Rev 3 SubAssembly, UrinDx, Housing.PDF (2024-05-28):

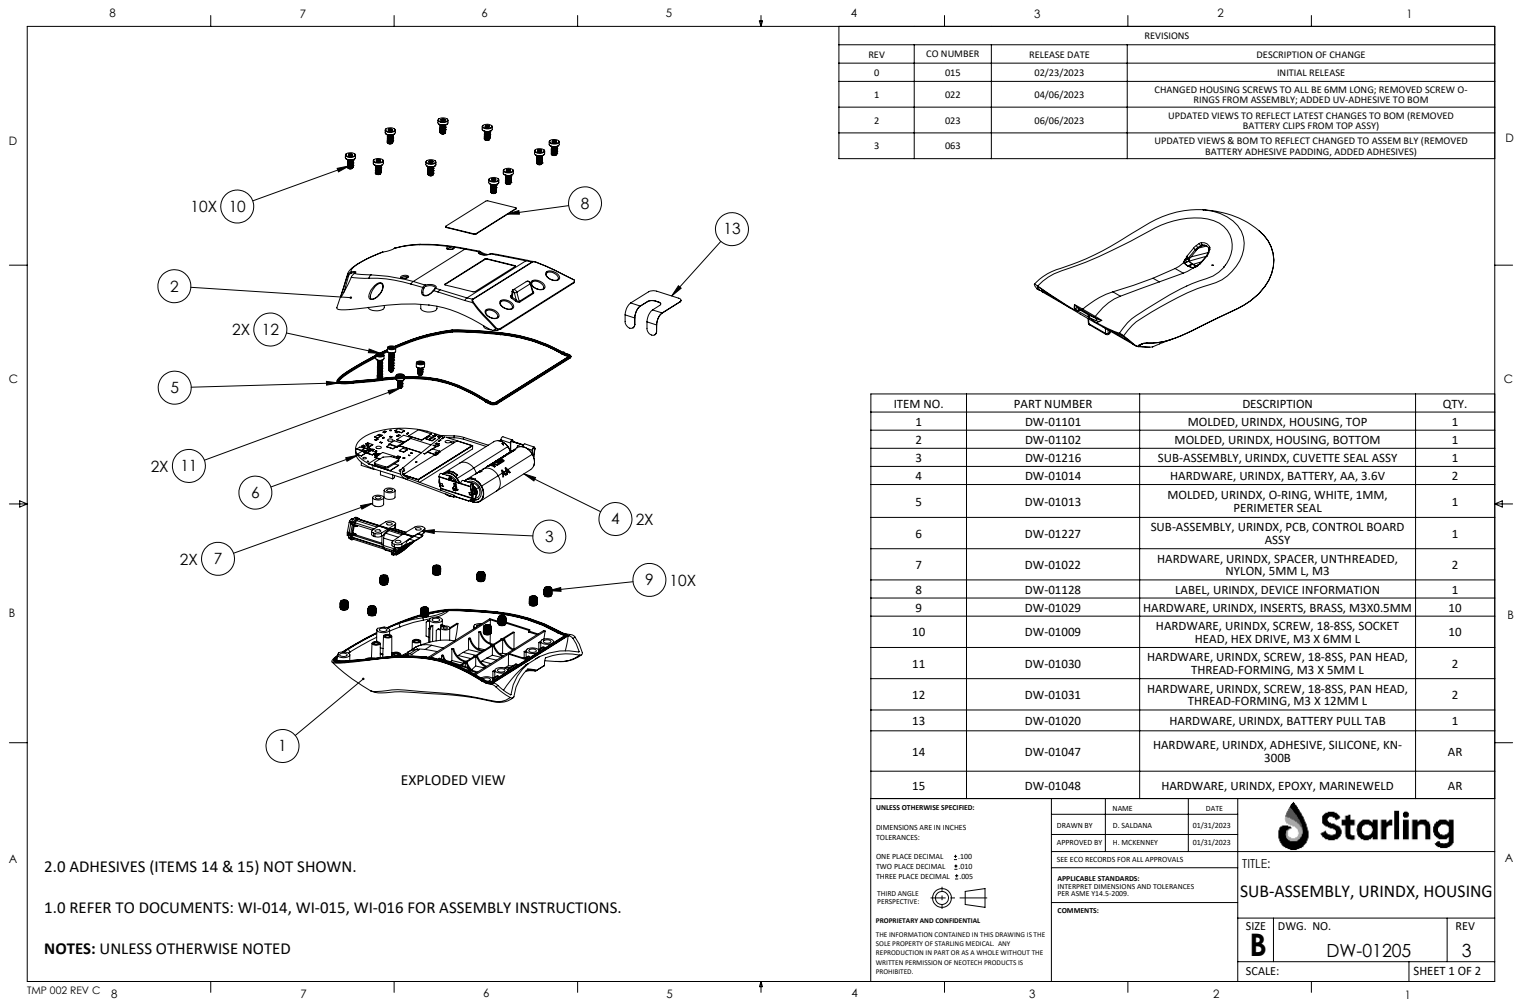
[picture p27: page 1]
EXPLODED VIEW; D. SALDANA; SHEET 1 OF 2; DWG. NO.; REV; TMP 002 REV C; ONE PLACE DECIMAL; TWO PLACE DECIMAL; THREE PLACE DECIMAL .005; APPLICABLE STANDARDS:; H. MCKENNEY

REV | CO NUMBER | RELEASE DATE | DESCRIPTION OF CHANGE
0 | 015 | 02/23/2023 | INITIAL RELEASE
1 | 022 | 04/06/2023 | CHANGED HOUSING SCREWS TO ALL BE 6MM LONG; REMOVED SCREW O-RINGS FROM ASSEMBLY; ADDED UV-ADHESIVE TO BOM
2 | 023 | 06/06/2023 | UPDATED VIEWS TO REFLECT LATEST CHANGES TO BOM (REMOVED BATTERY CLIPS FROM TOP ASSY)
3 | 063 | | UPDATED VIEWS & BOM TO REFLECT CHANGED TO ASSEM BLY (REMOVED BATTERY ADHESIVE PADDING, ADDED ADHESIVES)

ITEM NO. | PART NUMBER | DESCRIPTION | QTY.
1 | DW-01101 | MOLDED, URINDX, HOUSING, TOP | 1
2 | DW-01102 | MOLDED, URINDX, HOUSING, BOTTOM | 1
3 | DW-01216 | SUB-ASSEMBLY, URINDX, CUVETTE SEAL ASSY | 1
4 | DW-01014 | HARDWARE, URINDX, BATTERY, AA, 3.6V | 2
5 | DW-01013 | MOLDED, URINDX, O-RING, WHITE, 1MM, PERIMETER SEAL | 1
6 | DW-01227 | SUB-ASSEMBLY, URINDX, PCB, CONTROL BOARD ASSY | 1
7 | DW-01022 | HARDWARE, URINDX, SPACER, UNTHREADED, NYLON, 5MM L, M3 | 2
8 | DW-01128 | LABEL, URINDX, DEVICE INFORMATION | 1
9 | DW-01029 | HARDWARE, URINDX, INSERTS, BRASS, M3X0.5MM | 10
10 | DW-01009 | HARDWARE, URINDX, SCREW, 18-8SS, SOCKET HEAD, HEX DRIVE, M3 X 6MM L | 10
11 | DW-01030 | HARDWARE, URINDX, SCREW, 18-8SS, PAN HEAD, THREAD-FORMING, M3 X 5MM L | 2
12 | DW-01031 | HARDWARE, URINDX, SCREW, 18-8SS, PAN HEAD, THREAD-FORMING, M3 X 12MM L | 2
13 | DW-01020 | HARDWARE, URINDX, BATTERY PULL TAB | 1
14 | DW-01047 | HARDWARE, URINDX, ADHESIVE, SILICONE, KN-300B | AR

15 | DW-01048 | HARDWARE, URINDX, EPOXY, MARINEWELD | AR

UNLESS OTHERWISE SPECIFIED:
DIMENSIONS ARE IN INCHES
TOLERANCES:
THIRD ANGLE
PERSPECTIVE:
PROPRIETARY AND CONFIDENTIAL
THE INFORMATION CONTAINED IN THIS DRAWING IS THE
SOLE PROPERTY OF STARLING MEDICAL. ANY
REPRODUCTION IN PART OR AS A WHOLE WITHOUT THE
WRITTEN PERMISSION OF NEOTECH PRODUCTS IS
PROHIBITED.

DRAWN BY
APPROVED BY
SEE ECO RECORDS FOR ALL APPROVALS

2.0 ADHESIVES (ITEMS 14 & 15) NOT SHOWN.
1.0 REFER TO DOCUMENTS: WI-014, WI-015, WI-016 FOR ASSEMBLY INSTRUCTIONS.
NOTES: UNLESS OTHERWISE NOTED

TITLE:
SUB-ASSEMBLY, URINDX, HOUSING

INTERPRET DIMENSIONS AND TOLERANCES
PER ASME Y14.5-2009.
COMMENTS:

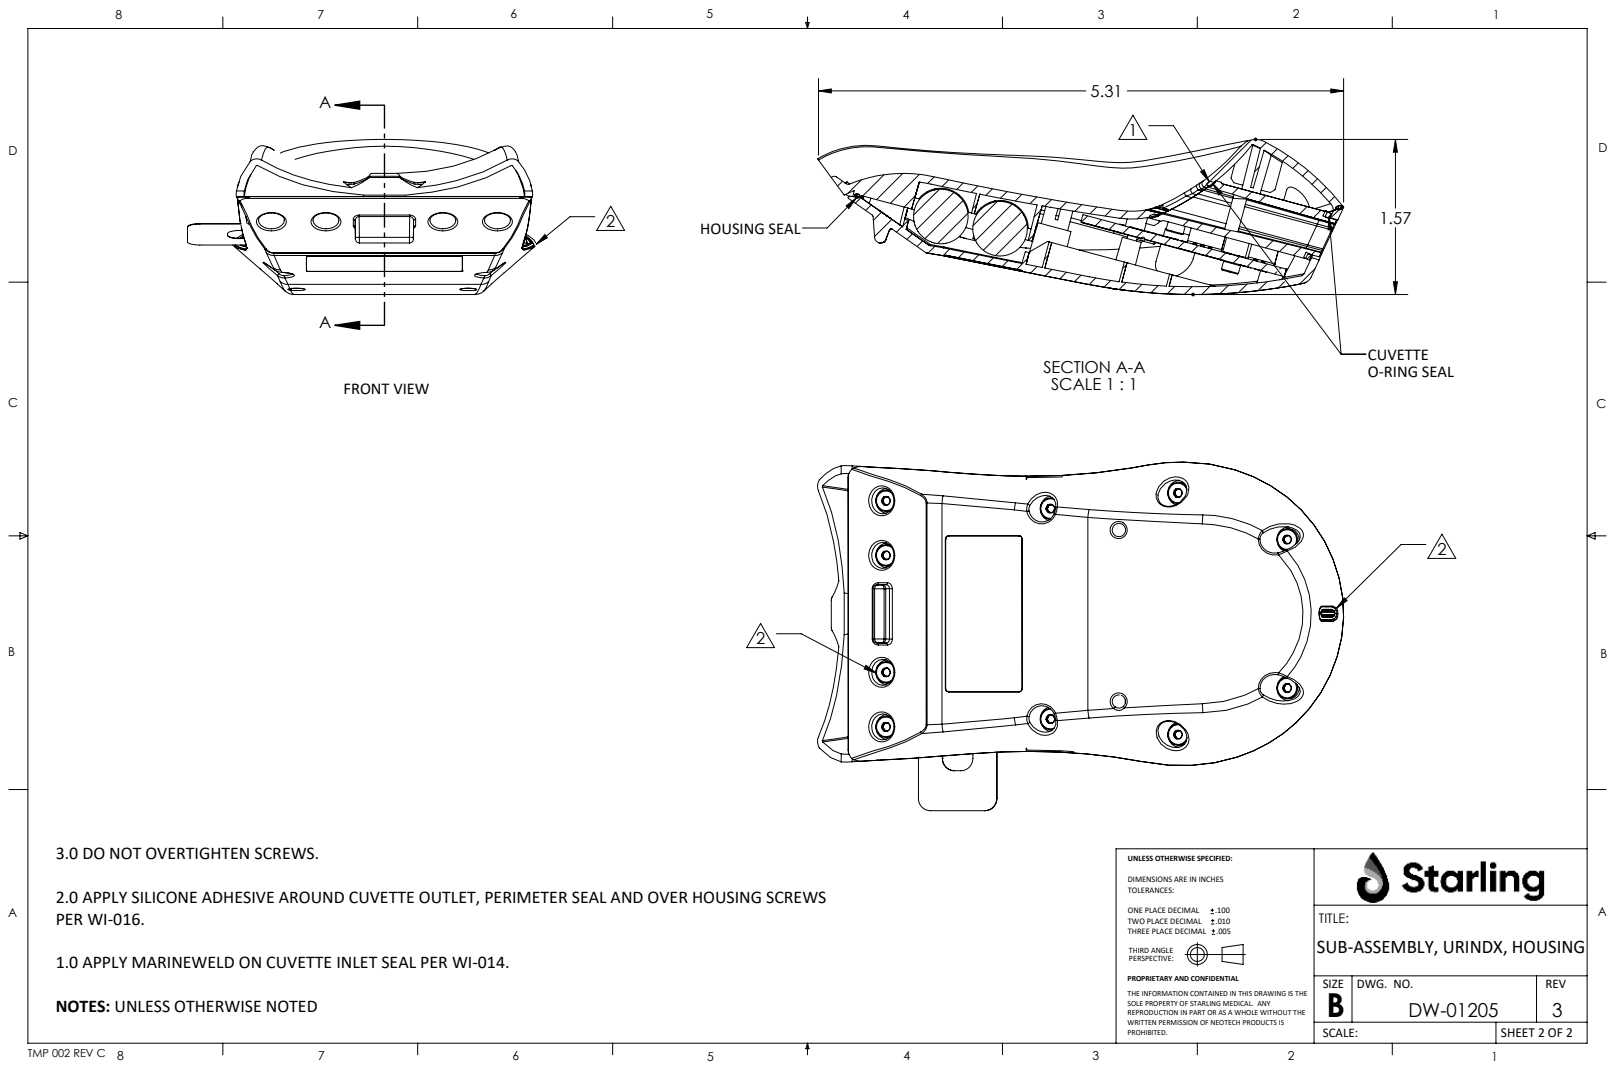
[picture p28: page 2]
FRONT VIEW; SECTION A-A SCALE 1 : 1; HOUSING SEAL; O-RING SEAL; SHEET 2 OF 2; DWG. NO.; REV; TMP 002 REV C; ONE PLACE DECIMAL; TWO PLACE DECIMAL

3.0 DO NOT OVERTIGHTEN SCREWS.
2.0 APPLY SILICONE ADHESIVE AROUND CUVETTE OUTLET, PERIMETER SEAL AND OVER HOUSING SCREWS
PER WI-016.
1.0 APPLY MARINEWELD ON CUVETTE INLET SEAL PER WI-014.
NOTES: UNLESS OTHERWISE NOTED

UNLESS OTHERWISE SPECIFIED:
DIMENSIONS ARE IN INCHES
TOLERANCES:
THREE PLACE DECIMAL .005
THIRD ANGLE
PERSPECTIVE:
PROPRIETARY AND CONFIDENTIAL
THE INFORMATION CONTAINED IN THIS DRAWING IS THE
SOLE PROPERTY OF STARLING MEDICAL. ANY
REPRODUCTION IN PART OR AS A WHOLE WITHOUT THE
WRITTEN PERMISSION OF NEOTECH PRODUCTS IS
PROHIBITED.

TITLE:
SUB-ASSEMBLY, URINDX, HOUSING

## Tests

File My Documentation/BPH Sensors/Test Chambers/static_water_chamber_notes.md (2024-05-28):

# How to Create a Static Water Test Chamber
## Starling Medical
### Ibrahim Al-Akash

# Static Water Test Chamber Notes

## Overview
The static water test chamber will be used to hold at least 100g of water while keeping the magnetometer sensor circuit safe from any leakage. To create a static water test chamber, first design the appropriate chamber geometry for the elastomer being tested, 3D print the design, assemble the testing apparatus, and inspect and iterate the waterproofing of the chamber.

## Design
The test chamber cross-sectional area should ideally be equal to the surface area of the elastomer being used in the experiment. This ensures that 100% of the mass of the water is being imparted onto the elastomer and that none of the load is transferred to the chamber itself. By meeting this criteria, the pressure on the elastomer is maximized, resulting in an increased sensitivity and a higher reslution sensing capability. A design with a larger cross-sectional area will require a taller chamber since a larger mass of water will be needed to impart enough force and pressure to compress the elastomer. Remember the equation $Pressure=\frac{Force}{Area}$.

## 3D Printing
1. Design the chamber in SolidWorks.
2. Save SolidWorks design as an `.STL` file and import to Chitubox software.
3. In Chitubox software, apply a tilt if possible to the model (for example rotate around z-axis by 45 degrees) and the add supports to model.
4. Ensure the correct resin profile is selected so that the profile matches the resin you will be printing with. Ensure the correct printer is selected in the Chitubox settings.
5. Slice the model and inspect it for any artifacts or errors. If there are errors, try rotating along a different axis and reapplying the supports.
6. Export the slice which will be a `.CTB` file to the directory of your choosing.
7. Upload the exported slice file to a USB flashdrive to send to the 3D printer.
8. Ensure the 3D printer has enough resin to print the parts.
9. Begin the print on the 3D printer.
10. When the 3D print is completed, carefully remove the parts from the plate by using the metal spatula. If the part is stuck, spray a little isopropyl alcohol on it and try again.
11. There should be 3 containers next to the 3D printers labeled `99% Isopropyl Alcohol`, `99% Isopropyl Alcohol (Contaminated)`, and `Diluted Green Wash`. Thoroughly clean the printed parts in each bucket in this order.
12. Set the parts next to the fan and wait ~5 minutes to dry.
13. Place the parts in the water cage in the container at the curing station. Remove the curing plate from the machine and place the water container in its place. Close the lid on it. Make sure the curing machine is set to rotation mode, not light mode. Set the time to 5:00 (6:00 if there are larger parts) and let the machine rinse the parts.
14. Once the rinse step is completed, set the parts next to the fan and wait 10 to 15 minutes until they are dry.
15. Once the parts are finished, place the curing plate on the curing machine. Ensure the magnets are aligned correctly so the plate is flush against the base. Ensure the curing machine is set to light mode. Set the time to 5:00.
16. Once the curing is completed, carefully remove the supports from the parts using pliers.

## Assembly
Thoroughly coat the outer surface of the test chamber with the waterproofing silicone adhesive paste. Let it dry for 10 to 30 minutes.

After assembling the elastomer-magnetometer apparatus according to the document titled `elastomer_creation_procedure.md` or `elastomer_creation_procedure.pdf`, apply superglue to the bottom surface of the test chamber and press the elastomer-magnetometer apparatus up into the chamber orifice. The elastomer should NOT be superglued, it should freely move within the chamber and should be snugly fit. Only the magnetometer sensor module PCB should be secured to the chamber. *This is a critical step I realized while assembling my last chamber for the Starling Medical Live Demo Showcase. If the elastomer is superglued inside the chamber, it will not compress properly and will result in faulty sensor readings.* Let the glue dry for 10 to 30 minutes.

## Waterproofing
Before attempting to perform the experiment, you must ensure that the chamber is adequately waterproofed to protect the sensor electronics. To do this, go to the sink and carefully begin adding water. After a decent amount of water is added, wait for at least 2 minutes and inspect the assembled testing apparatus for any leakage. Take note of any spots which are leaking and apply more waterproofing silicone adhesive paste to those areas.

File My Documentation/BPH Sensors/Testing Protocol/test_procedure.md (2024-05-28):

# Testing Protocol
## Starling Medical
### Ibrahim Al-Akash

# Procedure Overview:
To conduct a static water test for the magnetometer BPH sensor, you must first assemble the sensor circuit, set up the Arduino development environment, prepare the data logger, perform the appropriate experiment, clean the data log, and analyze the data.

## Sensor Circuit Assembly
First, assemble the magnetometer and elastomer assembly by following the instructions documented in the file `elastomer_creation_procedure.md` or `elastomer_creation_procedure.pdf`. To conduct the static water test using the MLX90393 magnetometer sensor and the HX711 load cell sensor, ensure that the circuit is wired properly before proceeding using the schematic below.

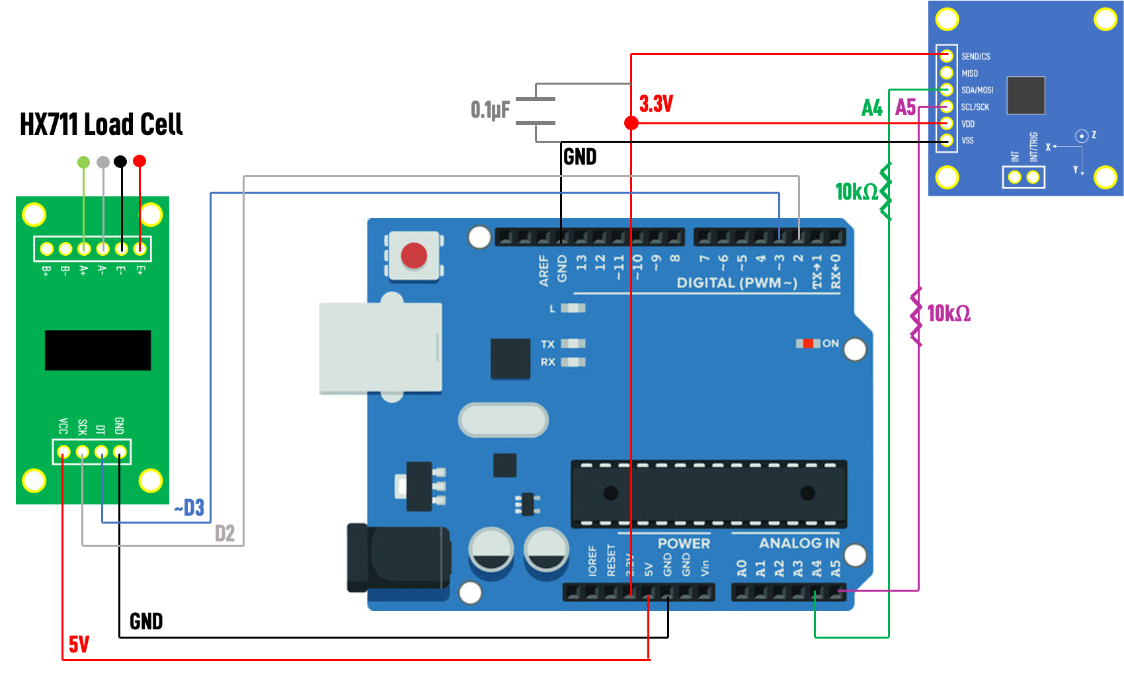
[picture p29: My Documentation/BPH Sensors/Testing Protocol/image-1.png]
Circuit Schematic


## Arduino Development Environment
After this, make sure that the library I made is imported to the Arduino IDE. The library is a folder called `Starling_MLX90393`. It is important that you use my library to interact with the magnetometer easily. DO NOT use any prebuilt libraries, they did not work. The prebuilt Adafruit library works, however it is very limited. My library takes advantage of many functions and settings built into the sensor's hardware. Then, open the file titled `starling_mlx90393_demo.ino` and upload the code to the Arduino Uno. 

## Prepping Data Logger
Next, to collect the data from the Arduino and store it on the computer, first open the terminal (on a MacOS computer). Then navigate to the directory of your choice where you want to store the data using the `cd PATHNAME/FILENAME` command in the terminal and make a script file by pasting the code below into the terminal:

`script -a -t0 FILENAME.txt`

Then, when you are ready to begin the test, run the following code in the terminal:

`screen ARDUINO_PORT 115200`

The `ARDUINO_PORT` can be located in the Arduino IDE by navigating to the `TOOLS -> PORT` menu and finding the name associated with (Arduino Uno). For example, mine is `/dev/cu.usbmodem11301`. Do not include the "(Arduino Uno)" in the port name. The number 115200 is the baudrate specified in the Arduino `.INO` file uploaded to the Arduino Uno. If you change the baud rate, this number must be changed in the terminal command. After this command is submitted, the terminal will enter into "recording mode" and the Arduino will begin running the code. The terminal will now become the Serial monitor and everything written on the Serial monitor will be logged to the file specified in the script code above. 

## Performing an Experiment
Follow the onscreen instructions to calibrate the load sensor scale. Ensure you have the 10g lead weight nearby to do the calibration correctly. After calibration, press any key to begin collecting data. The data collected is in this format:

`Sample # || Time || X-Axis B-Field || Y-Axis B-Field || Z-Axis B-Field || Mass`

### Experiment Ideas
- **Ground Test** - Log magnetometer and mass data over the testing period WITHOUT the elastomer and WITHOUT adding any water. There is NO magnet in this experiment. You should expect to see a steady horizontal line in the B-field readings and a steady 0 line in the mass readings. This should remain steady given the environment is not disturbed during the experiment and the load cell is calibrated accurately.
- **Functionality Test** - Log magnetometer and mass data over the testing period while manually pressing down on the elastomer with your hand. You should see the magnetometer and mass data spiking as you press with a harder force.
- **Calibration Test** - Log magnetometer and mass data over the testing period. Start with an empty container of 0g of water and steadily inject increments of water over equal time intervals until 100g to 120g of water is added. Use this data to conduct a polynomial fit between mass and B-field readings.
- **Accuracy Test** - Log magnetometer and mass data over the testing period. Start with an empty container of 0g of water and steadily inject increments of water over equal time intervals until 100g to 120g of water is added. Input the B-field readings into the polynomial from the calibration test and compare to the true mass readings.
- **False Negative Test** - Log magnetometer and mass data over the testing period WITH the elastomer and without adding any water. There IS magnet in this experiment. You should expect to see a steady horizontal line in the B-field readings and a steady 0 line in the mass readings. This should remain steady given the environment is not disturbed during the experiment and the load cell is calibrated accurately.

When you are satisfied with the test, to stop simply press `ctrl+A` followed by `ctrl+K`. You will be asked if you are sure you want to kill the program. Press `Y`. Then, the terminal will exit the Serial monitor screen. Finally, press `ctrl+D` and the script will save the log to the file. NOTE: This data is not in a usable format yet, it needs to be cleaned. 

## Cleaning the Data Log
First, open the `.TXT` file you just created and the delete all the text that comes before the header line (the header line is this text: `Sample  Time[4CX[7CY[7CZ`). Then, delete all the text right after the last data point line. The text should look something like: 

```
[7mReally kill this window [y/n][27m[K
                                                                                                                      
[?1l>[37;1H
[?1049l[screen is terminating]
[1m[7m%[27m[1m[0m                                                                                                                     
 
]7;file://Andalusia-MacBook-Pro.local/Users/jordanianjoker/Desktop/Starling-Medical/Programs/Magnet%20BPH%20Sensor
[0m[27m[24m[J(base) jordanianjoker@Andalusia-MacBook-Pro Magnet BPH Sensor % [K[?2004h[?2004l

Saving session...
...saving history...truncating history files...
...completed.

Script done on Thu Aug 17 17:05:10 2023
```

After these 2 texts are removed, you must then run a Python file I made to clean the extraneous characters called `logger_cleaner.py`. Make sure you replace the directory, pathnames, and filenames with the appropriate names before running the script. This will generate a `.CSV` file of the filename specified in the code containing all the cleaned data. This `.CSV` file should be ready for data analysis. 

### Error Notes
Sometimes the Arduino might skip a `\t` character and it will mess up a line in the csv. You can find the specific line by making a for loop in Python that loops i in range(len(file_data)) and then print(i) followed by print(float(file_data[i][4])). When the erroneous line is encountered, the line number will be printed to the console and you can use a csv file editor to remove that row (I use Numbers on Mac). Keep doing this until all the erroneous rows are removed (it should only be a few rows).

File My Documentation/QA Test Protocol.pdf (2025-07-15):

Protocol for QA Test Apparatus

Files: The folder to open in the Arduino IDE with the latest firmware is titled “Urinator4000.ino” and is located in the “internal-utilities” GitHub repository.

How the Test Works: The test first has a cooldown period specified in the “setup_time” variable prior to initiating the first experiment. Once the cooldown timer has ended, the white LEDs will start blinking and after a small delay the motor should activate. The motor and LEDs are activated for a duration of time specified in the “void_duration” variable. Next, the LEDs and motors are deactivated and the system is idle for a duration of time specified in the “cycle_duration” variable. The system then cycles between voiding and idling until the experiment is complete for which the total duration is specified in the “test_duration” variable. Throughout the experiment there are indicator LEDs located on the face of the PCB (red, yellow, green). The meaning of the indicators are provided below:

Indicator LEDs:
Solid red LED = system is in cooldown setup period
Solid green LED = system is in active voiding period
Solid yellow LED = system is idling in between voiding periods
Blinking red LED = system has concluded the test

To Initiate Test: Plug in the 12V power cable first, and then plug in the USB to the Arduino. Ideally, the USB should be plugged into the computer with the Arduino IDE open and the Serial Monitor displayed to show the logs in real time, however, if the USB is connected to a simple power source the device will still run the same. Note: Ensure that the IDE has Arduino Nano selected as the board and the processor is ATmega328P

To Modify Test: The parameters for the timings are easily adjustable from the Arduino IDE, just make sure to upload the code to the board before running the test again.

To Restart Test: Either disconnect the USB cable from the Arduino and reconnect it or you can press the reset button on the Arduino (shown below):

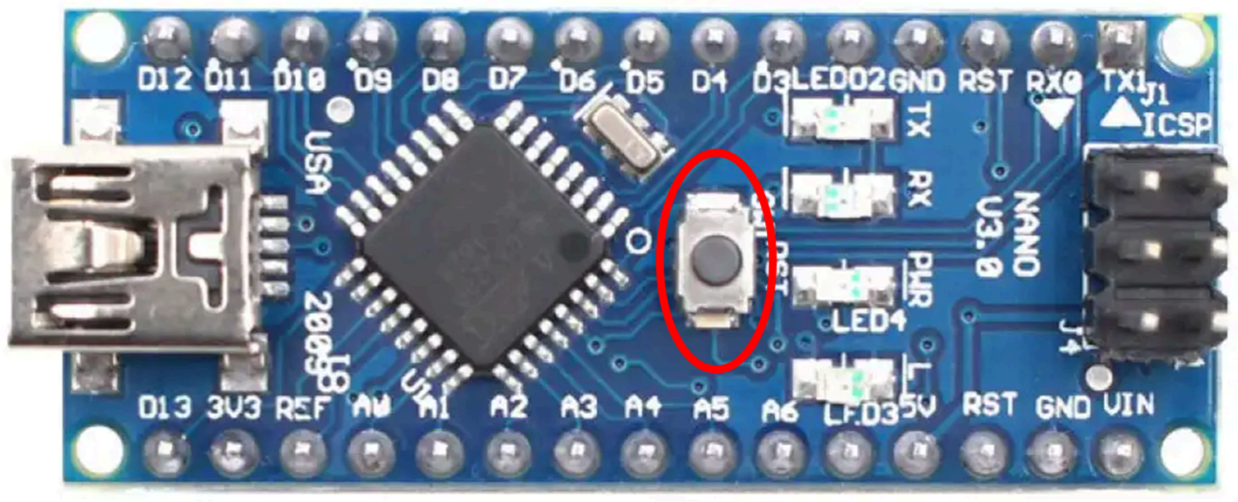
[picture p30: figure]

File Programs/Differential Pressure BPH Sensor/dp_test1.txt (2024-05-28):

Sample  Time[4CPressure[8CMass
1[7C24.1300 -0.16   0.01
2[7C24.2330 -0.18   -0.00
3[7C24.3370 -0.16   0.02
4[7C24.4390 -0.17   -0.00
5[7C24.5430 -0.16   0.02
6[7C24.6460 -0.18   0.00
7[7C24.7490 -0.16   0.00
8[7C24.8520 -0.16   0.02
9[7C24.9550 -0.18   0.01
10[6C25.0580 -0.16   0.03
11[6C25.1610 -0.17   0.03
12[6C25.2650 -0.16   0.03
13[6C25.3680 -0.18   0.03
14[6C25.4700 -0.16   0.04
15[6C25.5740 -0.18   0.03
16[6C25.6770 -0.16   0.03
17[6C25.7810 -0.18   0.03
18[6C25.8830 -0.16   0.03
19[6C25.9870 -0.18   0.03
20[6C26.0900 -0.16   0.04
21[6C26.1930 -0.16   0.02
22[6C26.2960 -0.18   0.01
23[6C26.3990 -0.16   0.01
24[6C26.5030 -0.18   0.02
25[6C26.6060 -0.16   0.03
26[6C26.7080 -0.18   0.02
27[6C26.8120 -0.16   0.02
28[6C26.9150 -0.18   -0.00
29[6C27.0190 -0.16   -0.04
30[6C27.1210 -0.18   -0.05
31[6C27.2250 -0.16   0.02
32[6C27.3280 -0.18   0.11
33[6C27.4310 -0.16   0.09
34[6C27.5340 -0.16   0.05
35[6C27.6370 -0.18   0.05
36[6C27.7410 -0.16   0.03
37[6C27.8440 -0.17   0.03
38[6C27.9480 -0.16   0.04
39[6C28.0500 -0.18   0.04
40[6C28.1530 -0.16   0.02
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

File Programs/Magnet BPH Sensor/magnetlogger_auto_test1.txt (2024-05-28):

1[7C24.85   -372.5580[7C-246.3690[7C7325.3403[7C10.0134
2[7C25.68   -378.5670[7C-252.3780[7C7324.1303[7C10.0133
3[7C26.58   -378.5670[7C-246.3690[7C7326.5502[7C9.9074
4[7C27.48   -372.5580[7C-246.3690[7C7332.6000[7C0.0030
5[7C28.38   -366.5490[7C-246.3690[7C7325.3403[7C-0.0328
6[7C29.28   -366.5490[7C-246.3690[7C7328.9702[7C-0.0296
7[7C30.19   -378.5670[7C-240.3600[7C7319.2900[7C-0.0409
8[7C31.09   -372.5580[7C-246.3690[7C7331.3901[7C-0.0247
9[7C31.99   -366.5490[7C-240.3600[7C7314.4501[7C-0.0323
10[6C32.89   -372.5580[7C-240.3600[7C7321.7104[7C-0.0334
11[6C33.79   -372.5580[7C-252.3780[7C7324.1303[7C-0.0243
12[6C34.70   -372.5580[7C-246.3690[7C7327.7602[7C-0.0243
13[6C35.60   -372.5580[7C-246.3690[7C7321.7104[7C-0.0225
14[6C36.50   -378.5670[7C-240.3600[7C7331.3901[7C-0.0218
15[6C37.40   -378.5670[7C-246.3690[7C7318.0800[7C-0.0153
16[6C38.30   -366.5490[7C-240.3600[7C7324.1303[7C-0.0216
17[6C39.21   -366.5490[7C-240.3600[7C7305.9804[7C-0.0209
18[6C40.11   -372.5580[7C-246.3690[7C7333.8100[7C-0.0214
19[6C41.01   -372.5580[7C-246.3690[7C7325.3403[7C-0.0183
20[6C41.91   -372.5580[7C-240.3600[7C7324.1303[7C-0.0159
21[6C42.81   -372.5580[7C-252.3780[7C7336.2304[7C-0.0136
22[6C43.72   -372.5580[7C-246.3690[7C7325.3403[7C-0.0191
23[6C44.62   -366.5490[7C-240.3600[7C7325.3403[7C-0.0164
24[6C45.52   -372.5580[7C-246.3690[7C7313.2402[7C-0.0225
25[6C46.42   -378.5670[7C-252.3780[7C7322.9204[7C-0.0154
26[6C47.33   -366.5490[7C-240.3600[7C7328.9702[7C-0.0174
27[6C48.23   -366.5490[7C-252.3780[7C7320.5000[7C-0.0102
28[6C49.13   -366.5490[7C-252.3780[7C7319.2900[7C-0.0047
29[6C50.03   -372.5580[7C-240.3600[7C7324.1303[7C1.0205
30[6C50.93   -372.5580[7C-246.3690[7C7333.8100[7C2.0251
31[6C51.84   -378.5670[7C-240.3600[7C7328.9702[7C2.0166
32[6C52.74   -378.5670[7C-252.3780[7C7319.2900[7C2.0211
33[6C53.64   -372.5580[7C-246.3690[7C7328.9702[7C2.0211
34[6C54.54   -372.5580[7C-240.3600[7C7308.4003[7C2.0182
35[6C55.44   -372.5580[7C-252.3780[7C7320.5000[7C2.0202
36[6C56.35   -372.5580[7C-246.3690[7C7320.5000[7C2.0133
37[6C57.25   -366.5490[7C-246.3690[7C7310.8203[7C2.0176
38[6C58.15   -372.5580[7C-246.3690[7C7328.9702[7C2.0156
39[6C59.05   -372.5580[7C-246.3690[7C7313.2402[7C2.0141
40[6C59.96   -372.5580[7C-246.3690[7C7325.3403[7C2.0132
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

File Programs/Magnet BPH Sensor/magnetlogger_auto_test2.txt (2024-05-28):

Sample,Time,X,Y,Z,Mass
1[7C16.05   -378.5670[7C-258.3870[7C7370.1103[7C0.1068
2[7C16.85   -372.5580[7C-252.3780[7C7360.4301[7C0.1079
3[7C17.75   -378.5670[7C-252.3780[7C7374.9501[7C0.1117
4[7C18.65   -372.5580[7C-252.3780[7C7365.2700[7C0.1136
5[7C19.56   -372.5580[7C-252.3780[7C7367.6904[7C0.1216
6[7C20.46   -378.5670[7C-252.3780[7C7373.7402[7C0.1074
7[7C21.36   -378.5670[7C-252.3780[7C7373.7402[7C0.1022
8[7C22.26   -372.5580[7C-246.3690[7C7359.2202[7C0.0900
9[7C23.17   -378.5670[7C-258.3870[7C7373.7402[7C0.1086
10[6C24.07   -372.5580[7C-246.3690[7C7366.4804[7C0.1135
11[6C24.97   -378.5670[7C-252.3780[7C7359.2202[7C0.1141
12[6C25.87   -378.5670[7C-252.3780[7C7358.0102[7C0.0441
13[6C26.78   -378.5670[7C-258.3870[7C7368.9003[7C0.0478
14[6C27.68   -378.5670[7C-246.3690[7C7372.5302[7C0.0456
15[6C28.58   -384.5760[7C-246.3690[7C7358.0102[7C0.8853
16[6C29.49   -366.5490[7C-252.3780[7C7376.1601[7C0.8006
17[6C30.39   -366.5490[7C-258.3870[7C7372.5302[7C0.7497
18[6C31.29   -372.5580[7C-252.3780[7C7373.7402[7C0.7271
19[6C32.19   -378.5670[7C-252.3780[7C7361.6401[7C0.6526
20[6C33.10   -366.5490[7C-258.3870[7C7373.7402[7C0.1349
21[6C34.00   -378.5670[7C-258.3870[7C7366.4804[7C0.0900
22[6C34.90   -372.5580[7C-258.3870[7C7378.5800[7C0.1646
23[6C35.81   -378.5670[7C-252.3780[7C7371.3203[7C0.0361
24[6C36.71   -372.5580[7C-252.3780[7C7364.0600[7C0.0477
25[6C37.61   -372.5580[7C-258.3870[7C7367.6904[7C0.0478
26[6C38.51   -378.5670[7C-252.3780[7C7364.0600[7C0.0359
27[6C39.42   -372.5580[7C-264.3960[7C7376.1601[7C0.0287
28[6C40.32   -378.5670[7C-252.3780[7C7367.6904[7C0.0259
29[6C41.22   -378.5670[7C-252.3780[7C7367.6904[7C0.0314
30[6C42.12   -378.5670[7C-258.3870[7C7373.7402[7C0.0256
31[6C43.03   -378.5670[7C-252.3780[7C7367.6904[7C0.0183
32[6C43.93   -366.5490[7C-246.3690[7C7359.2202[7C0.0167
33[6C44.83   -378.5670[7C-258.3870[7C7365.2700[7C0.0060
34[6C45.73   -372.5580[7C-258.3870[7C7372.5302[7C0.0151
35[6C46.64   -372.5580[7C-252.3780[7C7365.2700[7C0.0039
36[6C47.54   -372.5580[7C-252.3780[7C7366.4804[7C-0.0047
37[6C48.44   -366.5490[7C-258.3870[7C7373.7402[7C0.0003
38[6C49.35   -378.5670[7C-252.3780[7C7356.8002[7C0.0139
39[6C50.25   -372.5580[7C-252.3780[7C7372.5302[7C0.0122
40[6C51.15   -372.5580[7C-258.3870[7C7373.7402[7C-0.0033
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

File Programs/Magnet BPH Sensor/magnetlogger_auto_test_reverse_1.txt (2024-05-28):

Sample  Time[4CX[7CY[7CZ[7CMass
1[7C21.55   -360.5400[7C-264.3960[7C7344.7001[7C0.6098
2[7C22.34   -366.5490[7C-246.3690[7C7362.8500[7C0.6041
3[7C23.24   -366.5490[7C-252.3780[7C7354.3803[7C0.6027
4[7C24.14   -366.5490[7C-258.3870[7C7356.8002[7C0.6138
5[7C25.04   -366.5490[7C-252.3780[7C7354.3803[7C0.6133
6[7C25.94   -366.5490[7C-252.3780[7C7356.8002[7C0.6171
7[7C26.85   -372.5580[7C-252.3780[7C7351.9604[7C0.6245
8[7C27.75   -360.5400[7C-258.3870[7C7347.1201[7C0.6235
9[7C28.65   -372.5580[7C-252.3780[7C7342.2802[7C0.6230
10[6C29.55   -360.5400[7C-252.3780[7C7362.8500[7C0.6230
11[6C30.45   -366.5490[7C-252.3780[7C7356.8002[7C0.6131
12[6C31.36   -366.5490[7C-252.3780[7C7343.4902[7C0.6068
13[6C32.26   -360.5400[7C-252.3780[7C7355.5903[7C0.6023
14[6C33.16   -372.5580[7C-252.3780[7C7361.6401[7C0.6135
15[6C34.06   -366.5490[7C-252.3780[7C7362.8500[7C0.6031
16[6C34.96   -366.5490[7C-252.3780[7C7362.8500[7C0.6081
17[6C35.87   -366.5490[7C-258.3870[7C7358.0102[7C0.5985
18[6C36.77   -366.5490[7C-252.3780[7C7351.9604[7C0.5982
19[6C37.67   -366.5490[7C-252.3780[7C7349.5400[7C0.5949
20[6C38.57   -366.5490[7C-246.3690[7C7361.6401[7C0.5865
21[6C39.47   -366.5490[7C-252.3780[7C7358.0102[7C0.5889
22[6C40.38   -354.5310[7C-252.3780[7C7341.0703[7C0.5836
23[6C41.28   -366.5490[7C-252.3780[7C7359.2202[7C0.5770
24[6C42.18   -366.5490[7C-258.3870[7C7360.4301[7C0.5428
25[6C43.08   -366.5490[7C-252.3780[7C7353.1704[7C0.5572
26[6C43.98   -366.5490[7C-246.3690[7C7356.8002[7C0.6394
27[6C44.89   -366.5490[7C-252.3780[7C7359.2202[7C0.5757
28[6C45.79   -372.5580[7C-264.3960[7C7348.3300[7C0.5787
29[6C46.69   -366.5490[7C-252.3780[7C7361.6401[7C0.5648
30[6C47.59   -372.5580[7C-246.3690[7C7345.9101[7C0.5610
31[6C48.49   -366.5490[7C-252.3780[7C7359.2202[7C0.5702
32[6C49.39   -366.5490[7C-258.3870[7C7353.1704[7C0.5747
33[6C50.30   -366.5490[7C-252.3780[7C7349.5400[7C0.5660
34[6C51.20   -360.5400[7C-252.3780[7C7359.2202[7C0.5592
35[6C52.10   -366.5490[7C-258.3870[7C7359.2202[7C0.5735
36[6C53.00   -366.5490[7C-252.3780[7C7358.0102[7C0.5806
37[6C53.90   -360.5400[7C-252.3780[7C7351.9604[7C0.6665
38[6C54.81   -366.5490[7C-252.3780[7C7358.0102[7C0.6959
39[6C55.71   -360.5400[7C-252.3780[7C7362.8500[7C0.6907
40[6C56.61   -366.5490[7C-252.3780[7C7354.3803[7C0.6880
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

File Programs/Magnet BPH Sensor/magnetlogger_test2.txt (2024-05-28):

Time[4CX[7CY[7CZ
0.00[4C351.4680[8C516.6880[8C-2329.2500[6C
10.06   348.4640[8C519.6920[8C-2330.4599[6C
20.13   351.4680[8C519.6920[8C-2331.0651[6C
30.19   351.4680[8C519.6920[8C-2332.2751[6C
40.26   351.4680[8C519.6920[8C-2334.0900[6C
50.32   351.4680[8C519.6920[8C-2334.6950[6C
60.38   351.4680[8C519.6920[8C-2334.6950[6C
70.45   351.4680[8C519.6920[8C-2334.6950[6C
80.51   351.4680[8C519.6920[8C-2334.6950[6C
90.57   351.4680[8C522.6960[8C-2335.3000[6C
100.64  351.4680[8C519.6920[8C-2335.9050[6C
110.70  351.4680[8C519.6920[8C-2338.3251[6C
120.77  351.4680[8C519.6920[8C-2337.1149[6C

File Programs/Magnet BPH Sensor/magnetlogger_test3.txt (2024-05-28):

Time[4CX[7CY[7CZ
0.00[4C159.2120[8C-102.1360[7C3544.0900[7C
15.06   156.2080[8C-99.1320[8C3538.6450[7C
30.13   156.2080[8C-102.1360[7C3542.2751[7C
45.19   156.2080[8C-102.1360[7C3539.2500[7C
60.26   159.2120[8C-102.1360[7C3542.2751[7C
75.32   156.2080[8C-102.1360[7C3543.4851[7C
90.38   156.2080[8C-102.1360[7C3541.0651[7C
105.45  156.2080[8C-102.1360[7C3540.4602[7C
120.51  156.2080[8C-102.1360[7C3544.0900[7C
135.58  156.2080[8C-99.1320[8C3542.8801[7C
150.64  156.2080[8C-102.1360[7C3535.0151[7C
165.70  156.2080[8C-102.1360[7C3531.3850[7C
180.77  156.2080[8C-102.1360[7C3535.0151[7C
195.83  156.2080[8C-102.1360[7C3530.7800[7C
210.89  156.2080[8C-102.1360[7C3535.0151[7C
225.96  156.2080[8C-99.1320[8C3531.9899[7C
241.02  156.2080[8C-99.1320[8C3532.5952[7C

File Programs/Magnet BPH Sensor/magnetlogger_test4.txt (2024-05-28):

Sample  Time[4CX[7CY[7CZ
1[7C92.52   -126.1680[7C-114.1520[7C-5588.3852[6C
2[7C131.08  -126.1680[7C-114.1520[7C-5591.4101[6C
3[7C175.65  -126.1680[7C-114.1520[7C-5590.2001[6C
4[7C218.22  -126.1680[7C-114.1520[7C-5588.9902[6C
5[7C218.79  -126.1680[7C-114.1520[7C-5589.5952[6C
6[7C257.85  -126.1680[7C-114.1520[7C-5587.1752[6C
7[7C301.92  -126.1680[7C-114.1520[7C-5584.7553[6C
8[7C337.49  -126.1680[7C-114.1520[7C-5584.7553[6C
9[7C372.06  -126.1680[7C-114.1520[7C-5584.7553[6C
10[6C425.63  -123.1640[7C-114.1520[7C-5587.1752[6C
11[6C454.69  -123.1640[7C-114.1520[7C-5585.3603[6C
12[6C493.76  -126.1680[7C-114.1520[7C-5583.5454[6C
13[6C532.33  -126.1680[7C-114.1520[7C-5584.1503[6C
14[6C565.90  -123.1640[7C-114.1520[7C-5581.1250[6C
15[6C636.97  -123.1640[7C-114.1520[7C-5581.7299[6C
16[6C684.53  -126.1680[7C-114.1520[7C-5579.9150[6C
17[6C719.10  -123.1640[7C-114.1520[7C-5578.7050[6C
18[6C758.67  -123.1640[7C-114.1520[7C-5581.1250[6C
19[6C919.75  -123.1640[7C-114.1520[7C-5582.3349[6C
20[6C962.32  -123.1640[7C-114.1520[7C-5576.8901[6C
21[6C1011.39 -123.1640[7C-114.1520[7C-5576.2851[6C
22[6C1015.45 -123.1640[7C-114.1520[7C-5577.4951[6C
23[6C1077.52 -123.1640[7C-114.1520[7C-5579.3100[6C
24[6C1115.09 -123.1640[7C-114.1520[7C-5576.8901[6C
25[6C1147.16 -123.1640[7C-114.1520[7C-5577.4951[6C
26[6C1222.73 -123.1640[7C-114.1520[7C-5575.0751[6C
27[6C1267.80 -123.1640[7C-114.1520[7C-5576.8901[6C

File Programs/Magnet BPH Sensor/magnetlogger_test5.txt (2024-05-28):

Sample  Time[4CX[7CY[7CZ
1[7C231.53  171.2280[8C-138.1840[7C2438.7551[7C
2[7C292.60  171.2280[8C-138.1840[7C2438.1501[7C
3[7C349.67  171.2280[8C-138.1840[7C2442.3850[7C
4[7C387.24  171.2280[8C-138.1840[7C2444.8051[7C
5[7C442.31  171.2280[8C-138.1840[7C2447.8300[7C
6[7C494.88  174.2320[8C-141.1880[7C2449.6450[7C
7[7C550.95  171.2280[8C-141.1880[7C2451.4599[7C
8[7C597.01  171.2280[8C-141.1880[7C2452.0651[7C
9[7C657.08  174.2320[8C-141.1880[7C2452.6701[7C
10[6C680.15  171.2280[8C-141.1880[7C2451.4599[7C
11[6C736.72  171.2280[8C-141.1880[7C2451.4599[7C
12[6C780.79  171.2280[8C-141.1880[7C2450.8549[7C
13[6C831.36  171.2280[8C-141.1880[7C2450.2500[7C
14[6C870.42  171.2280[8C-141.1880[7C2450.8549[7C
15[6C905.99  171.2280[8C-141.1880[7C2450.2500[7C
16[6C947.56  171.2280[8C-141.1880[7C2451.4599[7C
17[6C984.63  174.2320[8C-141.1880[7C2450.8549[7C
18[6C1040.70 171.2280[8C-141.1880[7C2450.2500[7C
19[6C1077.27 171.2280[8C-141.1880[7C2450.8549[7C
20[6C1115.83 174.2320[8C-141.1880[7C2451.4599[7C
21[6C1143.40 171.2280[8C-141.1880[7C2450.2500[7C
22[6C1181.47 174.2320[8C-141.1880[7C2450.2500[7C
23[6C1235.54 171.2280[8C-141.1880[7C2449.6450[7C
24[6C1279.10 171.2280[8C-141.1880[7C2451.4599[7C
25[6C1308.67 174.2320[8C-141.1880[7C2451.4599[7C
26[6C1350.24 171.2280[8C-141.1880[7C2449.6450[7C
27[6C1382.31 171.2280[8C-141.1880[7C2450.2500[7C
28[6C1419.88 171.2280[8C-141.1880[7C2449.0400[7C
29[6C1448.94 171.2280[8C-141.1880[7C2449.0400[7C
30[6C1481.51 171.2280[8C-141.1880[7C2449.0400[7C
31[6C1522.08 171.2280[8C-141.1880[7C2448.4350[7C
32[6C1560.15 174.2320[8C-141.1880[7C2449.0400[7C
33[6C1592.21 171.2280[8C-141.1880[7C2447.8300[7C
34[6C1613.78 171.2280[8C-141.1880[7C2447.8300[7C
35[6C1649.85 171.2280[8C-141.1880[7C2447.8300[7C
36[6C1752.42 174.2320[8C-141.1880[7C2447.8300[7C
37[6C1788.49 174.2320[8C-141.1880[7C2447.8300[7C
38[6C1812.06 171.2280[8C-141.1880[7C2446.6201[7C
39[6C2035.14 171.2280[8C-141.1880[7C2448.4350[7C
40[6C2075.71 171.2280[8C-141.1880[7C2446.0151[7C
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

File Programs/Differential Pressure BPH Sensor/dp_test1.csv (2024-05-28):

Sample | Time | Pressure | Mass
1 | 24.1300 | -0.16 | 0.01
2 | 24.2330 | -0.18 | -0.00
3 | 24.3370 | -0.16 | 0.02
4 | 24.4390 | -0.17 | -0.00
5 | 24.5430 | -0.16 | 0.02
6 | 24.6460 | -0.18 | 0.00
7 | 24.7490 | -0.16 | 0.00
8 | 24.8520 | -0.16 | 0.02
9 | 24.9550 | -0.18 | 0.01
10 | 25.0580 | -0.16 | 0.03
11 | 25.1610 | -0.17 | 0.03
12 | 25.2650 | -0.16 | 0.03
13 | 25.3680 | -0.18 | 0.03
14 | 25.4700 | -0.16 | 0.04
15 | 25.5740 | -0.18 | 0.03
16 | 25.6770 | -0.16 | 0.03
17 | 25.7810 | -0.18 | 0.03
18 | 25.8830 | -0.16 | 0.03
19 | 25.9870 | -0.18 | 0.03
20 | 26.0900 | -0.16 | 0.04
21 | 26.1930 | -0.16 | 0.02
22 | 26.2960 | -0.18 | 0.01
23 | 26.3990 | -0.16 | 0.01
24 | 26.5030 | -0.18 | 0.02
25 | 26.6060 | -0.16 | 0.03
26 | 26.7080 | -0.18 | 0.02
27 | 26.8120 | -0.16 | 0.02
28 | 26.9150 | -0.18 | -0.00
29 | 27.0190 | -0.16 | -0.04
30 | 27.1210 | -0.18 | -0.05
31 | 27.2250 | -0.16 | 0.02
32 | 27.3280 | -0.18 | 0.11
33 | 27.4310 | -0.16 | 0.09
34 | 27.5340 | -0.16 | 0.05
35 | 27.6370 | -0.18 | 0.05
36 | 27.7410 | -0.16 | 0.03
37 | 27.8440 | -0.17 | 0.03
38 | 27.9480 | -0.16 | 0.04
39 | 28.0500 | -0.18 | 0.04
40 | 28.1530 | -0.16 | 0.02
41 | 28.2570 | -0.18 | 0.03
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

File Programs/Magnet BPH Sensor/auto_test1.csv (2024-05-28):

Sample | Time | X | Y | Z | Mass
1 | 24.85 | -372.5580 | -246.3690 | 7325.3403 | 10.0134
2 | 25.68 | -378.5670 | -252.3780 | 7324.1303 | 10.0133
3 | 26.58 | -378.5670 | -246.3690 | 7326.5502 | 9.9074
4 | 27.48 | -372.5580 | -246.3690 | 7332.6000 | 0.0030
5 | 28.38 | -366.5490 | -246.3690 | 7325.3403 | -0.0328
6 | 29.28 | -366.5490 | -246.3690 | 7328.9702 | -0.0296
7 | 30.19 | -378.5670 | -240.3600 | 7319.2900 | -0.0409
8 | 31.09 | -372.5580 | -246.3690 | 7331.3901 | -0.0247
9 | 31.99 | -366.5490 | -240.3600 | 7314.4501 | -0.0323
10 | 32.89 | -372.5580 | -240.3600 | 7321.7104 | -0.0334
11 | 33.79 | -372.5580 | -252.3780 | 7324.1303 | -0.0243
12 | 34.70 | -372.5580 | -246.3690 | 7327.7602 | -0.0243
13 | 35.60 | -372.5580 | -246.3690 | 7321.7104 | -0.0225
14 | 36.50 | -378.5670 | -240.3600 | 7331.3901 | -0.0218
15 | 37.40 | -378.5670 | -246.3690 | 7318.0800 | -0.0153
16 | 38.30 | -366.5490 | -240.3600 | 7324.1303 | -0.0216
17 | 39.21 | -366.5490 | -240.3600 | 7305.9804 | -0.0209
18 | 40.11 | -372.5580 | -246.3690 | 7333.8100 | -0.0214
19 | 41.01 | -372.5580 | -246.3690 | 7325.3403 | -0.0183
20 | 41.91 | -372.5580 | -240.3600 | 7324.1303 | -0.0159
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

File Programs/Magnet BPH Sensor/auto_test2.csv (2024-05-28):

Sample | Time | X | Y | Z | Mass
1 | 16.05 | -378.5670 | -258.3870 | 7370.1103 | 0.1068
2 | 16.85 | -372.5580 | -252.3780 | 7360.4301 | 0.1079
3 | 17.75 | -378.5670 | -252.3780 | 7374.9501 | 0.1117
4 | 18.65 | -372.5580 | -252.3780 | 7365.2700 | 0.1136
5 | 19.56 | -372.5580 | -252.3780 | 7367.6904 | 0.1216
6 | 20.46 | -378.5670 | -252.3780 | 7373.7402 | 0.1074
7 | 21.36 | -378.5670 | -252.3780 | 7373.7402 | 0.1022
8 | 22.26 | -372.5580 | -246.3690 | 7359.2202 | 0.0900
9 | 23.17 | -378.5670 | -258.3870 | 7373.7402 | 0.1086
10 | 24.07 | -372.5580 | -246.3690 | 7366.4804 | 0.1135
11 | 24.97 | -378.5670 | -252.3780 | 7359.2202 | 0.1141
12 | 25.87 | -378.5670 | -252.3780 | 7358.0102 | 0.0441
13 | 26.78 | -378.5670 | -258.3870 | 7368.9003 | 0.0478
14 | 27.68 | -378.5670 | -246.3690 | 7372.5302 | 0.0456
15 | 28.58 | -384.5760 | -246.3690 | 7358.0102 | 0.8853
16 | 29.49 | -366.5490 | -252.3780 | 7376.1601 | 0.8006
17 | 30.39 | -366.5490 | -258.3870 | 7372.5302 | 0.7497
18 | 31.29 | -372.5580 | -252.3780 | 7373.7402 | 0.7271
19 | 32.19 | -378.5670 | -252.3780 | 7361.6401 | 0.6526
20 | 33.10 | -366.5490 | -258.3870 | 7373.7402 | 0.1349
21 | 34.00 | -378.5670 | -258.3870 | 7366.4804 | 0.0900
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

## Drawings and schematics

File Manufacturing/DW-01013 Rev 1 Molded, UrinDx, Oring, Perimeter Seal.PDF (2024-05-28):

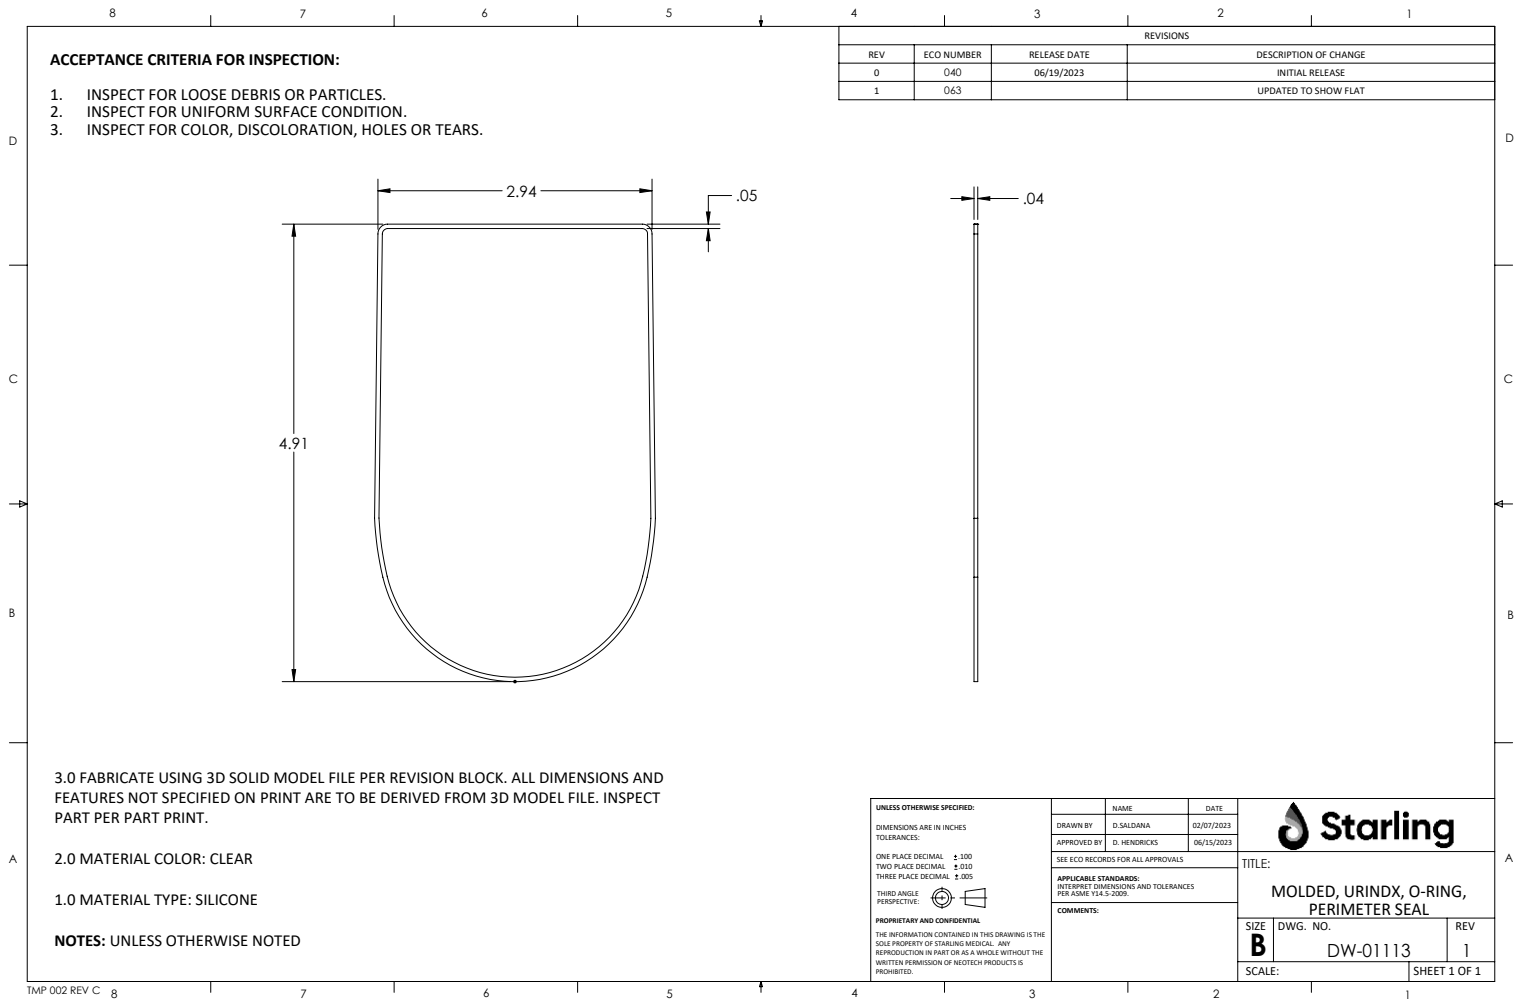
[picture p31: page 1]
SHEET 1 OF 1; DWG. NO.; REV; TMP 002 REV C; ONE PLACE DECIMAL; TWO PLACE DECIMAL; THREE PLACE DECIMAL .005; APPLICABLE STANDARDS:; D. HENDRICKS

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

REV | ECO NUMBER | RELEASE DATE | DESCRIPTION OF CHANGE
0 | 040 | 06/19/2023 | INITIAL RELEASE
1 | 063 | | UPDATED TO SHOW FLAT

3.0 FABRICATE USING 3D SOLID MODEL FILE PER REVISION BLOCK. ALL DIMENSIONS AND
FEATURES NOT SPECIFIED ON PRINT ARE TO BE DERIVED FROM 3D MODEL FILE. INSPECT
PART PER PART PRINT.
2.0 MATERIAL COLOR: CLEAR
1.0 MATERIAL TYPE: SILICONE
NOTES: UNLESS OTHERWISE NOTED

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

DRAWN BY
APPROVED BY
SEE ECO RECORDS FOR ALL APPROVALS

TITLE:
MOLDED, URINDX, O-RING,
PERIMETER SEAL

INTERPRET DIMENSIONS AND TOLERANCES
PER ASME Y14.5-2009.
COMMENTS:

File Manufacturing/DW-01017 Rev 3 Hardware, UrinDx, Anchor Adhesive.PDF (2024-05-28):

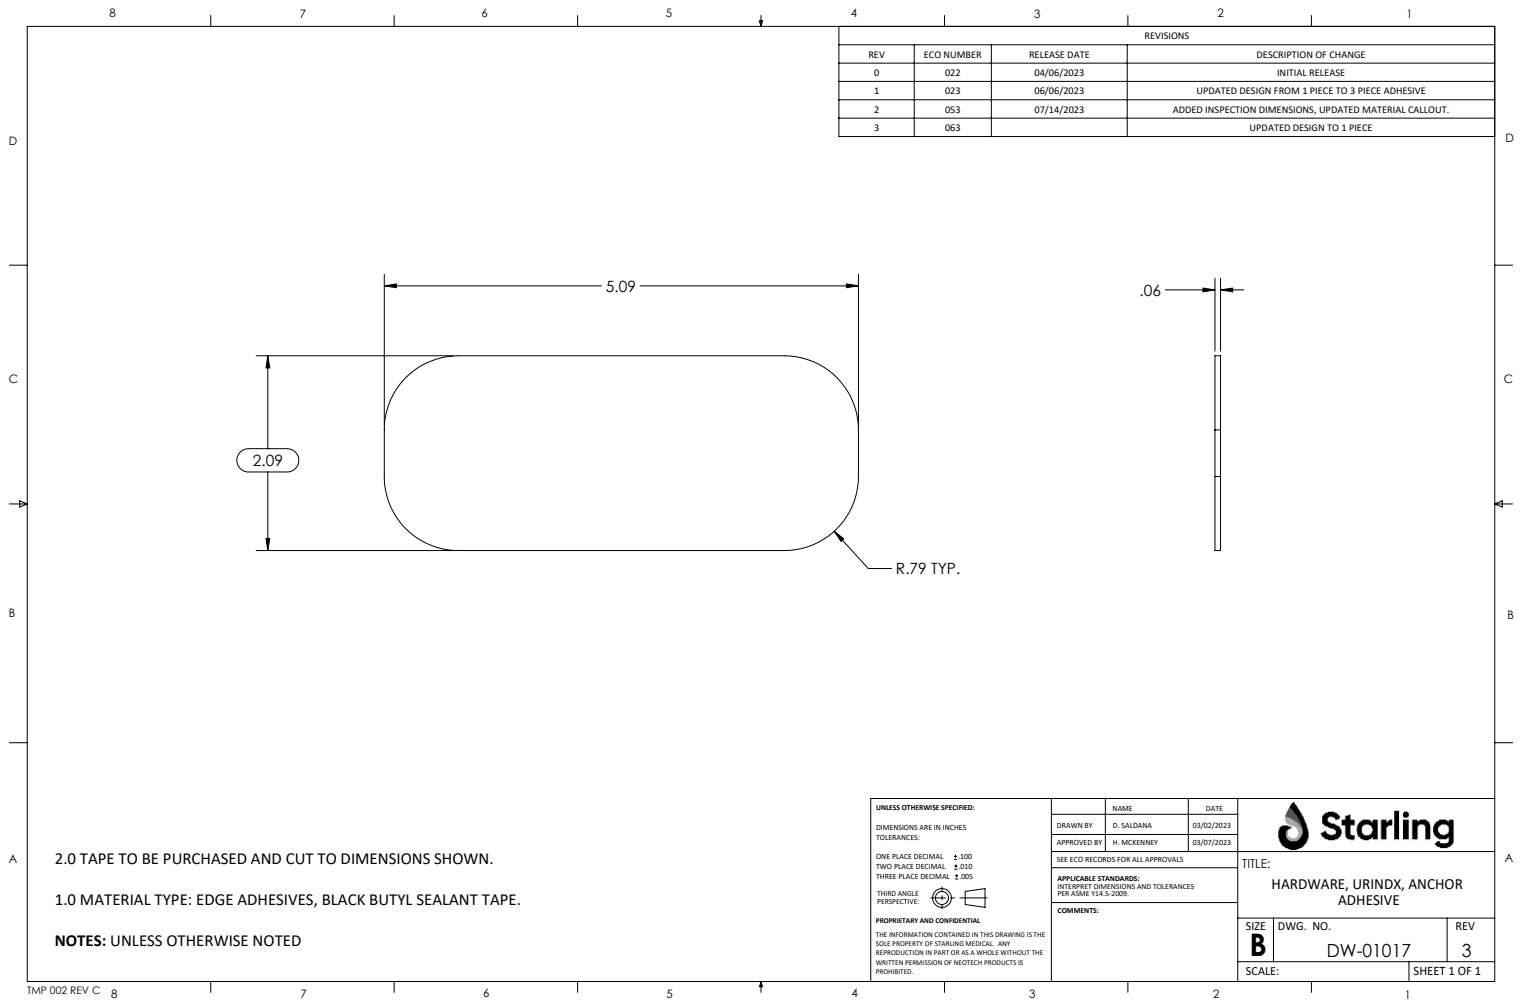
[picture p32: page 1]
R.79 TYP.; D. SALDANA; SHEET 1 OF 1; DWG. NO.; REV; HARDWARE, URINDX, ANCHOR; TMP 002 REV C; ONE PLACE DECIMAL; TWO PLACE DECIMAL; THREE PLACE DECIMAL .005; APPLICABLE STANDARDS:; H. MCKENNEY

REV | ECO NUMBER | RELEASE DATE | DESCRIPTION OF CHANGE
0 | 022 | 04/06/2023 | INITIAL RELEASE
1 | 023 | 06/06/2023 | UPDATED DESIGN FROM 1 PIECE TO 3 PIECE ADHESIVE
2 | 053 | 07/14/2023 | ADDED INSPECTION DIMENSIONS, UPDATED MATERIAL CALLOUT.
3 | 063 | | UPDATED DESIGN TO 1 PIECE

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

DRAWN BY
APPROVED BY
SEE ECO RECORDS FOR ALL APPROVALS

2.0 TAPE TO BE PURCHASED AND CUT TO DIMENSIONS SHOWN.
1.0 MATERIAL TYPE: EDGE ADHESIVES, BLACK BUTYL SEALANT TAPE.
NOTES: UNLESS OTHERWISE NOTED

INTERPRET DIMENSIONS AND TOLERANCES
PER ASME Y14.5-2009.
COMMENTS:

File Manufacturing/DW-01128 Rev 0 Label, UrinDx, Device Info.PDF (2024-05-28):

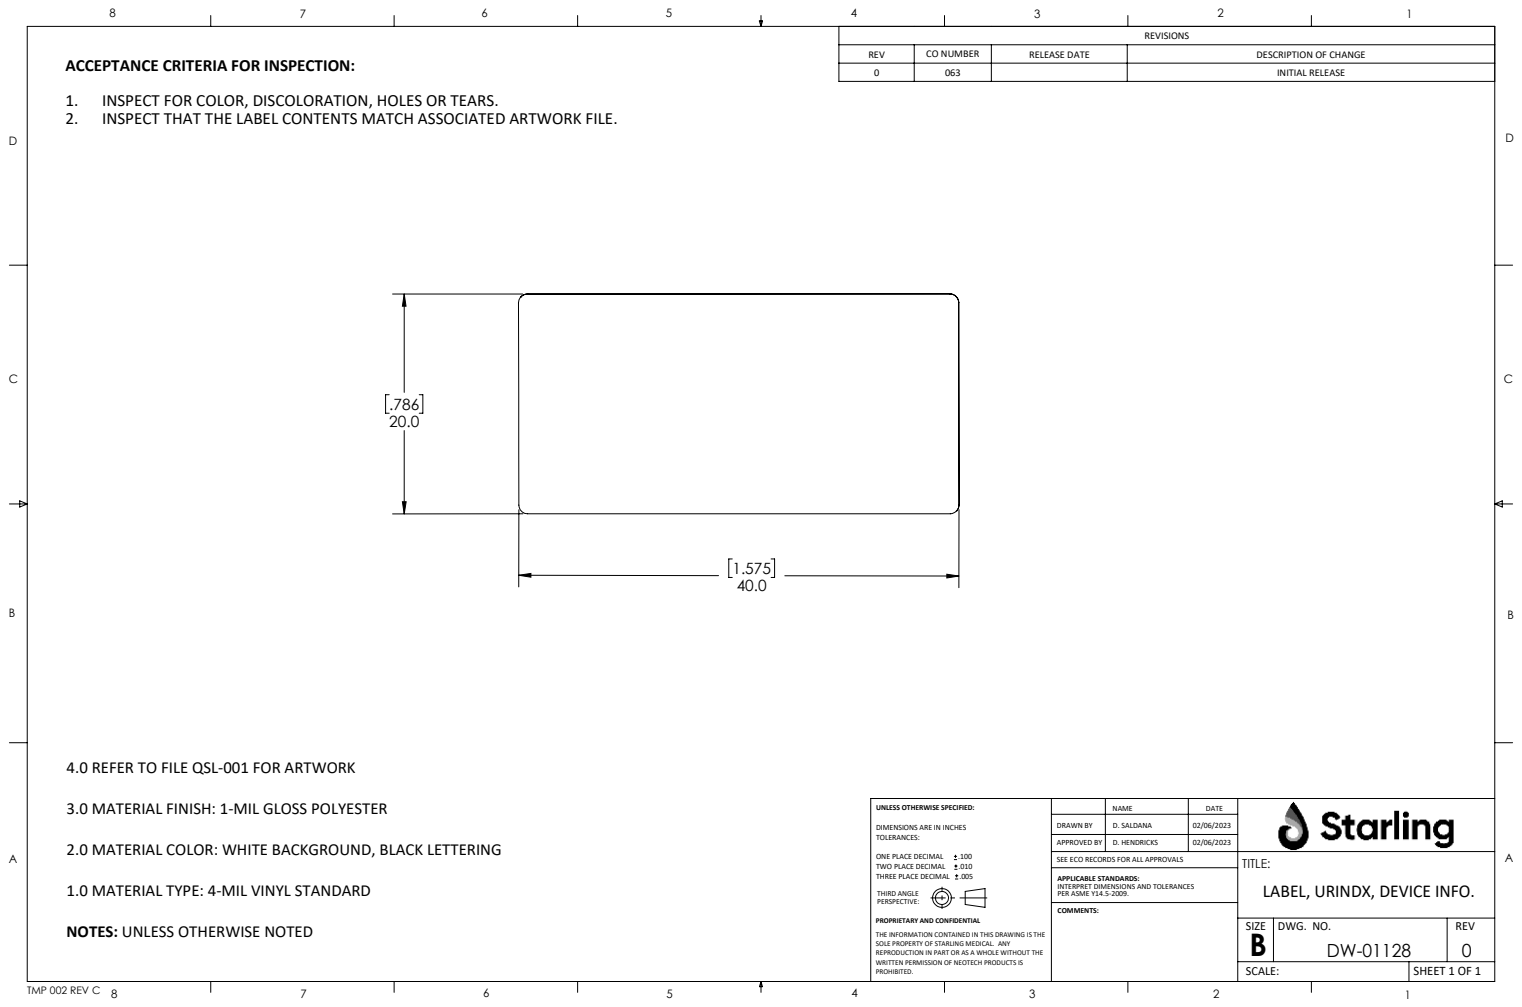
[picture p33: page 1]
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

REV | CO NUMBER | RELEASE DATE | DESCRIPTION OF CHANGE
0 | 063 | | INITIAL RELEASE

ACCEPTANCE CRITERIA FOR INSPECTION:
1. INSPECT FOR COLOR, DISCOLORATION, HOLES OR TEARS.
2. INSPECT THAT THE LABEL CONTENTS MATCH ASSOCIATED ARTWORK FILE.

4.0 REFER TO FILE QSL-001 FOR ARTWORK
3.0 MATERIAL FINISH: 1-MIL GLOSS POLYESTER
2.0 MATERIAL COLOR: WHITE BACKGROUND, BLACK LETTERING
1.0 MATERIAL TYPE: 4-MIL VINYL STANDARD
NOTES: UNLESS OTHERWISE NOTED

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

DRAWN BY
APPROVED BY
SEE ECO RECORDS FOR ALL APPROVALS

TITLE:
LABEL, URINDX, DEVICE INFO.

INTERPRET DIMENSIONS AND TOLERANCES
PER ASME Y14.5-2009.
COMMENTS:

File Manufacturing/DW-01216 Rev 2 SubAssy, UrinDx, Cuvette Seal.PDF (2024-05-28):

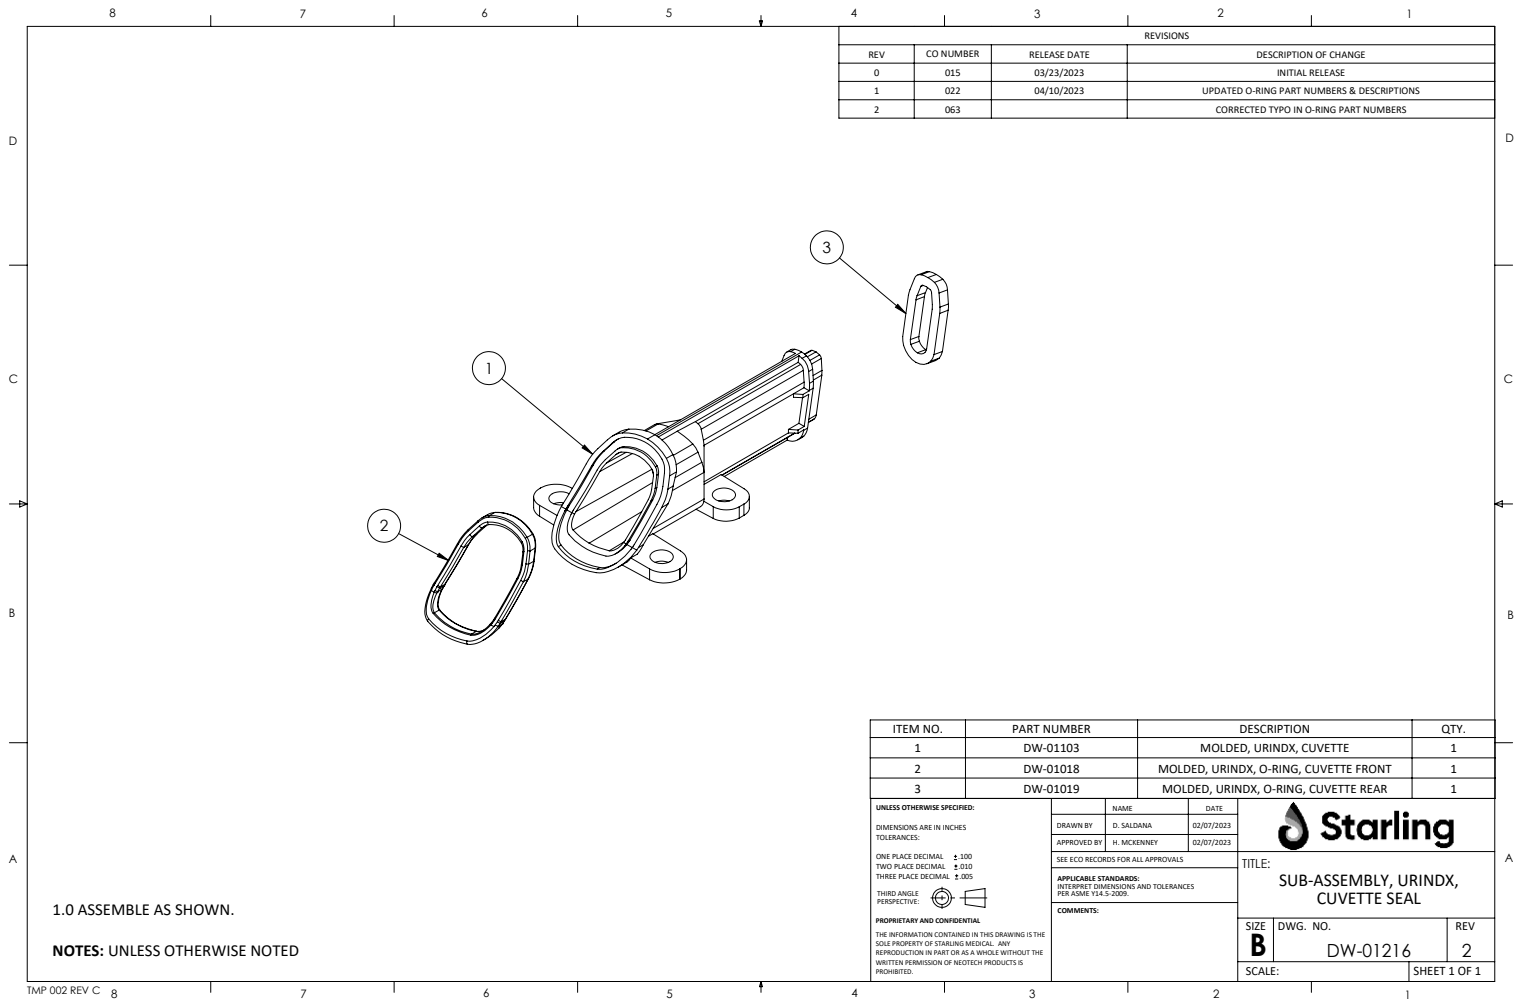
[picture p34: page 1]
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

REV | CO NUMBER | RELEASE DATE | DESCRIPTION OF CHANGE
0 | 015 | 03/23/2023 | INITIAL RELEASE
1 | 022 | 04/10/2023 | UPDATED O-RING PART NUMBERS & DESCRIPTIONS
2 | 063 | | CORRECTED TYPO IN O-RING PART NUMBERS

ITEM NO. | PART NUMBER | DESCRIPTION | QTY.
1 | DW-01103 | MOLDED, URINDX, CUVETTE | 1
2 | DW-01018 | MOLDED, URINDX, O-RING, CUVETTE FRONT | 1
3 | DW-01019 | MOLDED, URINDX, O-RING, CUVETTE REAR | 1

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

DRAWN BY
APPROVED BY
SEE ECO RECORDS FOR ALL APPROVALS

TITLE:
SUB-ASSEMBLY, URINDX,
CUVETTE SEAL

INTERPRET DIMENSIONS AND TOLERANCES
PER ASME Y14.5-2009.
COMMENTS:

1.0 ASSEMBLE AS SHOWN.
NOTES: UNLESS OTHERWISE NOTED

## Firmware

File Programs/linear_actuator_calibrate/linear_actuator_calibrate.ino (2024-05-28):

// Define pin connections & motor's steps per revolution
const int dirPin = 2;
const int stepPin = 3;
//const int stepsPerRevolution = 5000;
const int togglePin = 4;

//const int dirPin = 27;
//const int stepPin = 33;
//const int togglePin = 15;
int state = 0;

void setup()
{
  // Declare pins as Outputs
  pinMode(stepPin, OUTPUT);
  pinMode(dirPin, OUTPUT);
  pinMode(togglePin, INPUT);
  Serial.begin(250000);
}

void loop()
{
  // Call moveRev()
  if (digitalRead(togglePin) == 0)
  {
    if (state == 0)
    {
      // Program in the refill volume
      int steps = 3500;
      accelUp(1, 8000, 5500, 500);
      moveRev(1, 5500, steps - 1000);
      accelDown(1, 5500, 8000, 500);
      delay(500);
    }
    if (state == 1)
    {
      // Program in the calibration run:
      moveRev(0, 30000, 550); // Calibrate rate of 4000
      // moveRev(0, 7500, 550); // 3500
      moveRev(0, 28000, 550); // 3100
      // moveRev(0, 6800, 550); // 2800
      
      moveRev(0, 26000, 550); // 2500
      accelUp(0, 26000, 10000, 50); // These acceleration steps kick in to try to smooth out any binding
      // moveRev(0, 6200, 550); // 2200
      // accelUp(0, 6200, 6000, 106);
      
      moveRev(0, 10000, 250); // 2000
      accelUp(0, 10000, 4800, 350);
      // moveRev(0, 5800, 550); // 1800
      // accelUp(0, 5800, 5600, 106);

      
      moveRev(0, 4800, 550); // 1600
      accelUp(0, 4800, 4600, 75);
      // moveRev(0, 5400, 550); // 1400
      // accelUp(0, 5400, 5200, 106);
      
      moveRev(0, 4600, 550); // 1200
      // accelUp(0, 5200, 5000, 104);
      // moveRev(0, 5000, 550); // 1000
      
      
      delay(500);
    }

    // A purge for air to leave the chamber before the trial begins
    /*
    if (state == 2) 
    {
      // Place a purge that is of volume of the tube
    }
    */
    
    switch(state)
    {
      case 0:
        state = 1;
        // state = 2;
        break;
      case 1:
        state = 0;
        break;
      case 2:
        state = 1;
        break;
    }
  }
}

int moveRev(int dir, int per, int num_step)
{
  // dir: the direction to spin: 0 for CW, 1 for CCW
  // per: period of square wave output in microseconds
  // num_step: number of steps to go 

  if (dir == 0)
  {
    digitalWrite(dirPin, HIGH);
    for (int i = 0; i < num_step; i++)
    {
      digitalWrite(stepPin, HIGH);
      delayMicroseconds(round(per/2));
      digitalWrite(stepPin, LOW);
      delayMicroseconds(round(per/2));
    }
  }

  if (dir == 1)
  {
    digitalWrite(dirPin, LOW);
    for (int i = 0; i < num_step; i++)
    {
      digitalWrite(stepPin, HIGH);
      delayMicroseconds(round(per/2));
      digitalWrite(stepPin, LOW);
      delayMicroseconds(round(per/2));
    }
  }
  return(0);
}

float mapf(float x, float in_min, float in_max, float out_min, float out_max)
{
  return (x - in_min) * (out_max - out_min) / (in_max - in_min) + out_min;
}

void accelUp(int dir, float init, float fin, int num_step)
{
  // This function is marked as 'Attempt' due to the unsuccessful attempt to add higher or lower order polynomial
  // modelling to the uroflow curves
  // dir: the direction to spin: 0 for CW, 1 for CCW
  // init: initial period of square wave output in microseconds
  // fin: final period of square wave output in microseconds
  // num_step: the number of steps to run the acceleration curve through.
  // order: the polynomial order with which to fill the acceleration curve with
  // float scaled = pow(float(abs(init - fin)/num_step), order);
  if (dir == 0)
  {
    digitalWrite(dirPin, HIGH);
    float addedSpeed = 0.0;
    for (int i = 1; i < num_step; i++)
    {
      digitalWrite(stepPin, HIGH);
      delayMicroseconds((init - addedSpeed)/2);
      digitalWrite(stepPin, LOW);
      delayMicroseconds((init - addedSpeed)/2);
      addedSpeed = addedSpeed + float(abs(init - fin)/num_step);
      // Serial.println(addedSpeed);
    }
  }
  if (dir == 1)
  {
    digitalWrite(dirPin, LOW);
    float addedSpeed = 0.0;
    for (int i = 0; i < num_step; i++)
    {
      digitalWrite(stepPin, HIGH);
      delayMicroseconds((init - addedSpeed)/2);
      digitalWrite(stepPin, LOW);
      delayMicroseconds((init - addedSpeed)/2);
      addedSpeed = addedSpeed + float(abs(init - fin)/num_step);
      //Serial.println(addedSpeed);
    }
  }
  //return(0);
}

void accelUpAttempt(int dir, float init, float fin, int num_step, int order)
{
  // This function is marked as 'Attempt' due to the unsuccessful attempt to add higher or lower order polynomial
  // modelling to the uroflow curves
  // dir: the direction to spin: 0 for CW, 1 for CCW
  // init: initial period of square wave output in microseconds
  // fin: final period of square wave output in microseconds
  // num_step: the number of steps to run the acceleration curve through.
  // order: the polynomial order with which to fill the acceleration curve with
  // float scaled = pow(float(abs(init - fin)/num_step), order);
  if (dir == 0)
  {
    digitalWrite(dirPin, HIGH);
    float addedSpeed = 0.0;
    
    if (order == 1)
    {
      for (int i = 1; i < num_step; i++)
      {
      digitalWrite(stepPin, HIGH);
      delayMicroseconds((init - addedSpeed)/2);
      digitalWrite(stepPin, LOW);
      delayMicroseconds((init - addedSpeed)/2);
      addedSpeed = addedSpeed + pow(float(abs(init - fin)/num_step), order);
      // Serial.println(addedSpeed);
      }
    }

    if (order > 1)
    {
      int count = 1;
      // The plan is to generate an array of size of num_steps where
      // each element 
      float curveArray[num_step];
      for (int i = 1; i < num_step; i++)
      {
        // scaled = pow(scaled, order);        
        curveArray[count - 1] = pow(count, order);
        count = count + 1;
        Serial.println(count);
        Serial.println(curveArray[count - 1]);
      }

      // Map the example order array to the initial and final speed curves
      float mappedArray[num_step];
      for (int i = 0; i < (num_step - 1); i++)
      {
        mappedArray[i] = mapf(curveArray[i], 0, curveArray[num_step - 1], 0, abs(init - fin));
        Serial.println(count);
        Serial.println(curveArray[count - 1]);
      }
      
      for (int i = 0; i < (num_step - 1); i++)
      {
        digitalWrite(stepPin, HIGH);
        delayMicroseconds((init - mappedArray[i])/2);
        digitalWrite(stepPin, LOW);
        delayMicroseconds((init - mappedArray[i])/2);
        // The intuition here is to scale the straight line curve and then
        // scale it down with respect to the original scale of curve.
        // Based on just playing with the numbers, this appears to follow
        // a recurrence of x^order*(1/x^(order - 1))
        /*
        addedSpeed = scaled * (1/pow(count, order));
        Serial.println(addedSpeed);
        // Use counter to scale the increments of each step with respect to
        // the straight line,
        count = count + 1;
        scaled = count*(float(abs(init - fin)/num_step));
        scaled = pow(scaled, order);
        Serial.println(count);
        Serial.println(scaled);
        */
      }
    }
  }

  if (dir == 1)
  {
    digitalWrite(dirPin, LOW);
    float addedSpeed = 0.0;
    for (int i = 0; i < num_step; i++)
    {
      digitalWrite(stepPin, HIGH);
      delayMicroseconds((init - addedSpeed)/2);
      digitalWrite(stepPin, LOW);
      delayMicroseconds((init - addedSpeed)/2);
      addedSpeed = addedSpeed + float(abs(init - fin)/num_step);
      //Serial.println(addedSpeed);
    }
  }
  //return(0);
}

void accelDown(int dir, float init, float fin, int num_step)
{
  // dir: the direction to spin: 0 for CW, 1 for CCW
  // per: period of square wave output in microseconds
  // num_step: number of steps to go 

  if (dir == 0)
  {
    digitalWrite(dirPin, HIGH);
    float addedSpeed = 0.0;
    for (int i = 0; i < num_step; i++)
    {
      digitalWrite(stepPin, HIGH);
      delayMicroseconds((init + addedSpeed)/2);
      digitalWrite(stepPin, LOW);
      delayMicroseconds((init + addedSpeed)/2);
      addedSpeed = addedSpeed + float(abs(init - fin)/num_step);
      //Serial.println(addedSpeed);
    }
  }

  if (dir == 1)
  {
    digitalWrite(dirPin, LOW);
    float addedSpeed = 0.0;
    for (int i = 0; i < num_step; i++)
    {
      digitalWrite(stepPin, HIGH);
      delayMicroseconds((init + addedSpeed)/2);
      digitalWrite(stepPin, LOW);
      delayMicroseconds((init + addedSpeed)/2);
      addedSpeed = addedSpeed + float(abs(init - fin)/num_step);
      //Serial.println(addedSpeed);
    }
  }
  //return(0);
}

void flowAccelUp(int dir, float init, float fin, int vol)
{
  // dir: the direction to spin: 0 for CW, 1 for CCW
  // init: the number of steps per second initially
  // fin: the number of steps per second at the end
  // vol: amount of liquid volume to move through
  // order: order polynomial to fit the accel curve to
  int i_per = ((1/(init/0.0329)) * pow(10, 6));
  int f_per = ((1/(fin/0.0329)) * pow(10, 6));
  int steps = (vol * 30.395);
  if (dir == 0)
  {
    /*
    if (order == 1)
    {
       accelUp(0, i_per, f_per, steps, 1);
    }

    if (order != 1)
    {
      accelUp(0, i_per, f_per, steps, 2);
    }
    */
    accelUp(0, i_per, f_per, steps);
  }

  if (dir == 1)
  {
    /*
    if (order == 1)
    {
       accelUp(1, i_per, f_per, steps, 1);
    }

    if (order != 1)
    {
      accelUp(1, i_per, f_per, steps, 2);
    }
    */

    accelUp(1, i_per, f_per, steps);
  }
}

void flowAccelDown(int dir, float init, float fin, int vol)
{
  // dir: the direction to spin: 0 for CW, 1 for CCW
  // init: the initial flow rate
  // fin: the final flowrate
  // vol: amount of liquid volume to move through
  int i_per = ((1/(init/0.0329)) * pow(10, 6));
  int f_per = ((1/(fin/0.0329)) * pow(10, 6));
  int steps = (vol * 30.395);
  if (dir == 0)
  {
    accelDown(0, i_per, f_per, steps);
  }

  if (dir == 1)
  {
    accelDown(1, i_per, f_per, steps);
  }
}

void moveVol(int dir, float rate, int vol)
{
  int per = ((1/(rate/0.0329)) * pow(10, 6));
  int steps = (vol * 30.395);
  if (dir == 0)
  {
    moveRev(0, per, steps);
  }

  if (dir == 1)
  {
    moveRev(1, per, steps);
  }
}

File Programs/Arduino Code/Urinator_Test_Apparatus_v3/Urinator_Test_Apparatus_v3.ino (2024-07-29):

// Ibrahim Al-Akash
// Starling Medical
// QA Testing Apparatus V3
// 5-26-24

// Include the RTC Library:
#include <DS3231.h>

// Include the SD library:
#include <SPI.h>
#include <SD.h>

// Include the Flow Sensor Library
#include <Arduino.h>
#include <FlowSensor.h>

// Pin Layout
/*
SD CARD
--------
4: CS
11: MOSI
13: CLK
12: MISO

2: Flowmeter PIN
7: LED PIN
9: RELAY PIN
A0: Photoresistor PIN
A5: RTC SCL
A4: RTC SDA
*/

// Initiate the DS3231 using the hardware interface
DS3231  rtc(SDA, SCL);

unsigned long start_time;
unsigned long temp_time;
unsigned int setup_time = 10; // seconds (Duration system allows for tester to complete setup before running experiment)
unsigned int void_duration = 1; // seconds (Duration of urination simulation)
unsigned int cycle_duration = 9; // seconds (A cycle duration is the duration between each void)
unsigned int test_duration = 60; // seconds (Test duration is the entire duration of the experiment)
String current_time;
String log_filename;
Time t;
bool PUMP_STATUS = false;
bool LED_STATUS = false;

#define LED_PIN 7
#define RELAY_PIN 9
#define SD_CS_PIN 4
#define PHOTORESISTOR_PIN A0
#define type YFS201
#define FLOWSENSOR_PIN 2 // pin -> interrupt pin 

FlowSensor Sensor(type, FLOWSENSOR_PIN);

void setup()
{
  // Setup pin modes
  pinMode(LED_PIN, OUTPUT);
  pinMode(RELAY_PIN, OUTPUT);
  pinMode(PHOTORESISTOR_PIN, INPUT);

  // Setup Serial connection
  Serial.begin(9600);

  // Initialize SD card
  SD.begin(4);
  while (!Serial) {
    ; // wait for the serial port to connect. Needed for native USB port only
  }
  Serial.print("Initializing SD card...");
  while (!SD.begin(4)) {
    Serial.println("initialization failed!");
  }
  Serial.println("initialization done.");

  // Initialize the real-time clock object
  rtc.begin();

  // Initialize flowmeter counter
  Sensor.begin(count);

  // Generate log file
  log_filename = "LOG.txt";
  File dataFile = SD.open(log_filename.c_str(), FILE_WRITE);

  // Wait for the setup delay period to end and then proceed to running
  while(delta_time(start_time) < setup_time){}

  // Record the start time
  start_time = rtc.getUnixTime(rtc.getTime());
  Serial.print("Start Time: ");
  Serial.println(rtc.getTimeStr());
  dataFile.print("Start Time: ");
  dataFile.println(rtc.getTimeStr());

  // Initialize CSV header names
  dataFile.println("Time (s)\tLED Status (On/Off)\tPhotoresistor (V)\tPump Status (On/Off)\tFlow Rate (L/min)");
  dataFile.close();
  Serial.println("File Created");

  while(delta_time(start_time) < test_duration){
    // While the test is ongoing, run a void simulation at each cycle duration
    temp_time = rtc.getUnixTime(rtc.getTime());
    unsigned long end_time = temp_time + void_duration;
    while(delta_time(temp_time) < cycle_duration){
      // Log data for bookkeeping
      log_data(log_filename, start_time, LED_STATUS, analogRead(PHOTORESISTOR_PIN), PUMP_STATUS, read_flowmeter());
      // Run void simulation
      activate(void_duration, log_filename, start_time);
      delay(1000);
      log_data(log_filename, start_time, LED_STATUS, analogRead(PHOTORESISTOR_PIN), PUMP_STATUS, read_flowmeter());
      temp_time = rtc.getUnixTime(rtc.getTime());
      // Calculate remaining time until the next cycle
      unsigned long next_cycle_time = start_time + ((delta_time(temp_time) / cycle_duration) + 1) * cycle_duration;
      unsigned long remaining_time = next_cycle_time - rtc.getUnixTime(rtc.getTime());
      // Wait for the remaining time using the RTC
      while (delta_time(rtc.getUnixTime(rtc.getTime())) < remaining_time) {
        delay(1000);
        log_data(log_filename, start_time, LED_STATUS, analogRead(PHOTORESISTOR_PIN), PUMP_STATUS, read_flowmeter());
      }
      temp_time = rtc.getUnixTime(rtc.getTime());
    }
  }
  // Mark the conclusion of the test in the SD card data log
  dataFile = SD.open(log_filename.c_str(), FILE_WRITE);
  dataFile.print("-");
  dataFile.print("\t");
  dataFile.print("-");
  dataFile.print("\t");
  dataFile.print("-");
  dataFile.print("\t");
  dataFile.print("-");
  dataFile.print("\t");
  dataFile.println("-");
  dataFile.println("TEST COMPLETED");
  dataFile.print("END TIME: ");
  dataFile.println(rtc.getTimeStr());
  dataFile.close();
  Serial.println("TEST COMPLETED");
  while(1){}
  delay(100);
}

void loop()
{
  
}
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
